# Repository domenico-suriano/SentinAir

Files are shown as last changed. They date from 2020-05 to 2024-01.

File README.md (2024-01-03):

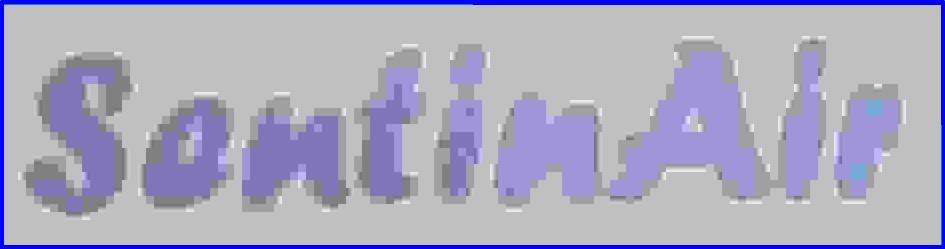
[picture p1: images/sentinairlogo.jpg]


Project designer and developer

Dr. Domenico Suriano , domenico.suriano@enea.it

# Description

SentinAir is a device designed for data acquisition from diverse types of instruments, sensors or devices. This system was at first developed for air pollutant monitoring activities, but it can also be used in other fields. Through this tool, you can acquire data from gas sensors or devices that you can plug into SentinAir system by USB, Ethernet, serial, or I2C ports. This system is useful especially in activities performed far from the laboratory facilities. The minimum requirement necessary to use the SentinAir device is a 220 Volt a.c. power source. The system can be controlled from the remote through internet wireless connections or through the Wi-Fi LAN set up by the SentinAir device as soon as it starts up. You can use SentinAir, for example, as a portable monitoring unit for air pollutant concentration detection; or, for evaluating device, instrument and sensor performances. By clicking on the pictures below you can see an explanatory video about the SentinAir use. You can find detailed information about how to set up and use SentinAir in the [user guide](https://github.com/domenico-suriano/SentinAir/blob/master/guide/sentinair-user-guide-2.0.pdf) released in the "guide" folder of this repository. The description of the SentinAir system and its use are also shown in four scientific articles: [A portable air quality monitoring unit and a modular, flexible tool for on-field evaluation and calibration of low-cost gas sensors](https://doi.org/10.1016/j.ohx.2021.e00198) published on HardwareX by Elsevier, [SentinAir system software: A flexible tool for data acquisition from heterogeneous sensors and devices](https://doi.org/10.1016/j.softx.2020.100589) published on "SoftwareX" by Elsevier, [Design and Development of a Flexible, Plug-and-Play, Cost-Effective Tool for on-Field Evaluation of Gas Sensors](https://doi.org/10.1155/2020/8812025) published on "Journal of Sensors" by Hindawi, and [Assessment of the Performance of a Low-Cost Air Quality Monitor in an Indoor Environment through Different Calibration Models](https://doi.org/10.3390/atmos13040567) published on "Atmosphere" by MDPI. I hope it will be useful to you.

# SentinAir software quick installation
This is a quick procedure to install the SentinAir software making the minimum steps. If you desire a higher level of customization, you can refer to the “SentinAir software installation” chapter of the [user guide](https://github.com/domenico-suriano/SentinAir/blob/master/guide/sentinair-user-guide-2.0.pdf) released in this repository. To install SentinAir, download the [last SentinAir SD card image file](https://drive.google.com/file/d/1KaBjFTMJjB79ryGpAMCCBvThq09m7BA6/view?usp=sharing) (file size of 720 Mb), unzip the file, then write it in a SD card having at least 2 GB of memory space (4GB recommended) by using, for example, Win32diskimage.exe program (for Windows operative systems). Finally, insert the SD card in the slot of the Raspberry PI board.

# Using SentinAir
After following the "quick installation" procedure, plug into one of the system ports your sensors/devices/instruments and give power to the device. Wait for a few of seconds, you will see the green light asynchronously blinking (this indicates that the system is starting up). After few seconds, the yellow light will start blinking fastly. This means that the system is performing the port scanning and the devices/sensor/instrument connection. Wait for few tens of seconds, then the red check light will turn on. When the yellow light stops blinking and turns on, the system is ready and it is already performing the data acquisition. To shut down SentinAir, press for few seconds the "stop button", then the yellow check light will start blinking. Wait for each light turns off, then unplug the power cable. For more detials to use the SentinAir system, please, refer to the [user guide](https://github.com/domenico-suriano/SentinAir/blob/master/guide/sentinair-user-guide-2.0.pdf) released in this repository. An overview of the SentinAir system use is shown in the video you can see by clicking on the pictures at the bottom of this page.
Here below are summarized the instruments which drivers have been already developed and incorporated in the sentinAIr software, and therefore, readily usable with sentinAir.
| Device | Device driver | Connection interface | Supplier or manufacturer |
|     :---:    |            :---:            |                      :---:                   |                         :---:                        |
|106L GO3 pro package (CO2and O3 monitor)|[go3.py](https://github.com/domenico-suriano/SentinAir/blob/master/sentinair/devices/go3.py)|USB|[2B technologies](https://www.twobtech.com)|
|405nm (NOx monitor)|[nox405.py ](https://github.com/domenico-suriano/SentinAir/blob/master/sentinair/devices/nox405.py)|USB|2B technologies|
|CO12M (CO chemical analyzer)|[co12m.py](https://github.com/domenico-suriano/SentinAir/blob/master/sentinair/devices/co12m.py) |Ethernet port|[Environnement](https://www.envea.global)|
|AF22M (SO2 chemical analyzer)|[af22.py ](https://github.com/domenico-suriano/SentinAir/blob/master/sentinair/devices/af22.py)|Ethernet port|Environnement|
|AC32M (NOx chemical analyzer)|[ac32.py](https://github.com/domenico-suriano/SentinAir/blob/master/sentinair/devices/ac32.py) |Ethernet port|Environnement|
|O342M (O3 chemical analyzer)|[o342.py](https://github.com/domenico-suriano/SentinAir/blob/master/sentinair/devices/o342.py) |Ethernet port|Environnement|
|VOC72M (VOCchemical analyzer)|[v72m.py](https://github.com/domenico-suriano/SentinAir/blob/master/sentinair/devices/v72m.py) |Ethernet port|Environnement|

Here below are listed the sensors having a I2C, TTL serial port, or USB hardware interface, which drivers have been already developed and incorporated in the sentinAIr software, and therefore, readily usable with sentinAir. This list does not include the sensors featured by only an analog output interface.

| Sensor | Sensor driver | Connection interface | Supplier or manufacturer |
|     :---:    |            :---:            |                      :---:                   |                         :---:                        |
|BME280 (atmospheric pressure, temperature, and relative humidity)|[bme280.py](https://github.com/domenico-suriano/SentinAir/blob/master/sentinair/devices/bme280.py)|I2C|[Bosch Sensortec](https://www.bosch-sensortec.com)|
|BH1750 (luxmeter)|[bh1750.py](https://github.com/domenico-suriano/SentinAir/blob/master/sentinair/devices/bh1750.py) |I2C|[ROHM semiconductor](https://www.rohm.com)|
|PMS5003 (PM sensor)|[pms5003.py](https://github.com/domenico-suriano/SentinAir/blob/master/sentinair/devices/pms5003.py) |TTL serial port|[Plantower](https://www.plantower.com/en/)|
|PMS3003 (PM sensor)|[pms3003.py ](https://github.com/domenico-suriano/SentinAir/blob/master/sentinair/devices/pms3003.py)|TTL serial port|Plantower|
|MHZ19 (CO2 sensor)|[mhz19.py](https://github.com/domenico-suriano/SentinAir/blob/master/sentinair/devices/mhz19.py) |TTL serial port|[Winsen](https://www.winsen-sensor.com)|
|IRC-A1 (CO2 sensor)|[irca1.py](https://github.com/domenico-suriano/SentinAir/blob/master/sentinair/devices/irca1.py) |USB|[Alphasense](https://www.alphasense.com/product_type/target-gas/)|
|SPS30 (PM sensor)|[sps30.py](https://github.com/domenico-suriano/SentinAir/blob/master/sentinair/devices/sps30.py) |TTL serial port|[Sensirion](https://sensirion.com)|

In order to use the sensors featured by just the analog hardware interface, drivers for some Analog-to-DIgital Converter (ADC) boards have been already developed and incorporated in the SentinAIr software. Currently, they are the [ADC Pi board](https://www.abelectronics.co.uk/p/69/adc-pi-raspberry-pi-analogue-to-digital-converter) (which driver is [mcp342x.py](https://github.com/domenico-suriano/SentinAir/blob/master/sentinair/devices/mcp342x.py)) by [ABelectronics](https://www.abelectronics.co.uk/), the [Multisensor board](https://www.tecnosens.it/en/multisensor) (which driver is [multisensor_board.py](https://github.com/domenico-suriano/SentinAir/blob/master/sentinair/devices/multisensor_board.py)) by [Tecnosens](https://www.tecnosens.it/en), and the Lcss adapter which is an open source project you can find [here](https://github.com/domenico-suriano/Lcss-adapter-board).

In the list shown below, there are some examples of sensors featured by an analog output signal that can be readily used in the SentinAir system. The list does not cover every sensor or device available on the market usable with SentinAir, because its purpose is just to provide an idea about the flexibility of the system proposed. Therefore, this is a partial list which wants to provide some examples. Moreover, we must consider that any analog sensor has to be used through its support board, usually provided by the manufacturer, or the supplier, or built by the user, and one of the boards acting as adapter to the SentinAir system, such as: the ADC Pi board, the LCSS adapter, or the Multisensor board.

| Sensor | Support board name | Adapter board| Sensor supplier or manufacturer |
|     :---:    |            :---:            |                      :---:                   |                         :---:                        |
|CO-BX (CO sensor)|[ISB by Alphasense](https://www.alphasense.com/products/support-circuits-air/) or [Alphasense-B4-multisensor-board](https://github.com/domenico-suriano/Alphasense-B4-multisensor-board) |ADC Pi or LCSS adapter|[Alphasense](https://www.alphasense.com)|
|NO2-B43F (NO2 sensor)|ISB by Alphasense or Alphasense-B4-multisensor-board|ADC Pi or LCSS adapter|Alphasense|
|NO-B4 (NO sensor)|ISB by Alphasense |ADC Pi or LCSS adapter|Alphasense|
|OX-B431 (O3 sensor)|ISB by Alphasense or Alphasense-B4-multisensor-board|ADC Pi or LCSS adapter|Alphasense|
|SO2-B4 (SO2 sensor)|ISB by Alphasense or Alphasense-B4-multisensor-board|ADC Pi or LCSS adapter|Alphasense|
|H2S-B4 (H2S sensor)|ISB by Alphasense or Alphasense-B4-multisensor-board|ADC Pi or LCSS adapter|Alphasense|
|CO-A4 (CO sensor)|[AFE by Alphasense](https://www.alphasense.com/products/support-circuits-air/)|ADC Pi or LCSS adapter|Alphasense|
|NO-A4 (NO sensor)|AFE by Alphasense|ADC Pi or LCSS adapter|Alphasense|
|SO2-A4 (SO2 sensor)|AFE by Alphasense|ADC Pi or LCSS adapter|Alphasense|
|OX-A431 (O3 sensor)|AFE by Alphasense|ADC Pi or LCSS adapter|Alphasense|
|H2S-A4 (H2S sensor)|AFE by Alphasense|ADC Pi or LCSS adapter|Alphasense|
|PID-A12 (VOC sensor)|AFE by Alphasense|ADC Pi or LCSS adapter|Alphasense|
|PID-AH2 (VOC sensor)|AFE by Alphasense|ADC Pi or LCSS adapter|Alphasense|
|GS+4CO (CO sensor)|[AFE by TEcnosens](https://www.tecnosens.it/en/application-sectors/multigas-monitor/multisensor-board)|[Multisensor board by Tecnosens](https://www.tecnosens.it/en/application-sectors/multigas-monitor/multisensor-board)|[DDScientific](https://www.ddscientific.com)|
|GS+4ETO (ETO sensor)|AFE by TEcnosens|Multisensor board by Tecnosens|DDScientific|
|GS+4NH3-100 (NH3 sensor)|AFE by TEcnosens|Multisensor board by Tecnosens|DDScientific|
|GS+4NO (NO sensor)|AFE by TEcnosens|Multisensor board by Tecnosens|DDScientific|
|GS+4NO2 (NO2 sensor)|AFE by TEcnosens|Multisensor board by Tecnosens|DDScientific|
|GS+4CL2 (Cl2 sensor)|AFE by TEcnosens|Multisensor board by Tecnosens|DDScientific|
|GS+4SO2 (SO2 sensor)|AFE by TEcnosens|Multisensor board by Tecnosens|DDScientific|
|TDS 0035(CH4 sensor)|AFE by TEcnosens|Multisensor board by Tecnosens|[Dynament](https://www.dynament.com/data-old/premier-series/)|
|TDS 0058(CO2 sensor)|AFE by TEcnosens|Multisensor board by Tecnosens|[Dynament](https://www.dynament.com/data-old/premier-series/)|
|SP61 (O3 sensor)|[A1320301-SP61-01 by Nissha](https://www.fisinc.co.jp/en/products/products_search.html?Cat=Cat2)|ADC Pi or LCSS adapter|[Nissha-Fis](https://www.fisinc.co.jp/en/)|
|SP61 (O3 sensor)|A1320301-SP61-02 by Nissha|ADC Pi|Nissha-Fis|
|SPS-AQ2-01 (VOC sensor)|EVM-SP-02-SP3S by Nissha|ADC Pi|Nissha-Fis|
|SB-xx (SB series sensor for various gases)|[EVM-SB-01-xx by Nissha](https://www.fisinc.co.jp/en/products/products_search.html?Cat=Cat2)|ADC Pi|Nissha-Fis|
|SP-xx (SP series sensor for various gases)|[EVM-SP-01-xx by Nissha](https://www.fisinc.co.jp/en/products/products_search.html?Cat=Cat2)|ADC Pi|Nissha-Fis|
|TGS26xx (TGS26 series sensor for various gases)|[EM26 by Figaro](https://www.figarosensor.com/product/evaluation-board/)|ADC Pi|[Figaro](https://www.figarosensor.com)|
|FECSxx (FECS series sensor for various gases)|[EM-FECS(B) by Figaro](https://www.figarosensor.com/product/evaluation-board/)|ADC Pi|Figaro|
|ME2-CO (CO sensor)|[ZE07-CO by Winsen](https://www.winsen-sensor.com/sensors/co-sensor/ze07-co.html)|ADC Pi or LCSS adapter|[Winsen](https://www.winsen-sensor.com/)|

# Last Updates

16 december 2023

-a) removed the lighttpd http server

-b) updated "sentinair-system-manager.py" to optimize the hourly and daily calulations, to incorporate the http server and to add the graphical user interface through the new web pages

-c) modified the structure of the sentinair software directories

-d) updated "sentinair-system-installer.py" to improve the "user-friendly" grade

26 september 2022

-a) updated "sentinair-system-manager.py" to fix a bug in logging the device scanning reports

-b) added the drivers for SPS30 (PM sensor), PMS5003 (PM sensor), and MHZ19 (CO2 sensor)

2 february 2021

-a) updated "sentinair-system-manager.py" to modify the check light behaviour

-b) added the driver for bme280 (temperature, humidity, and atmospheric pressure sensor)

11 november 2020:

-a) updated "sentinair-system-manager.py" to support I2C devices

-b) added drivers for bh1750 (luxmeter) and mcp342x (ADC Pi converter)

-c) updated the user guide. More clarifications and examples concerning "How to write new device drivers". Added information about the use of the ADC Pi.

-d) added device driver templates to facilitate the process of writing new device drivers (see the user guide).

-e) published the release of the version 1.2

-f) [SentinAir SD card image file](https://drive.google.com/file/d/1Ex4GyDE1UydjNPgzCsWaSeaUH6ddkkUb/view?usp=sharing) updated.

7 october 2020:

-a) minor bugs fixed.

-b) the red check light now blinks during the port scanning at start-up time.

-c) configuration of the module "imap-smtp-interface.py" by editing the file "mail-config.sentinair" (please refer to the [user guide](https://github.com/domenico-suriano/SentinAir/blob/master/guide/sentinair-system-user-guide.pdf) for details),

-d) User guide updated,

-e) release [sentinair_1.0.zip](https://github.com/domenico-suriano/SentinAir/releases/download/1.0/sentinair-1.0.zip) updated,

-f) [SentinAir SD card image file](https://drive.google.com/file/d/1AfPUjvr3tC3ymnK-TsBThjoi5kFb1ZuD/view?usp=sharing) updated.

30 september 2020:

-a) user guide updated,

-b) some minor bugs fixed.

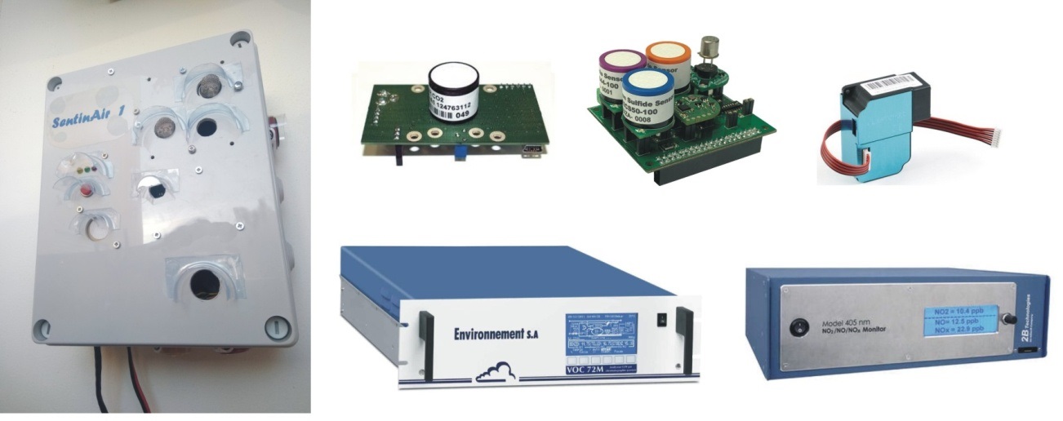
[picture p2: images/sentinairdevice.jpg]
sentinair (https://youtu.be/oAHfk2gzcIE)

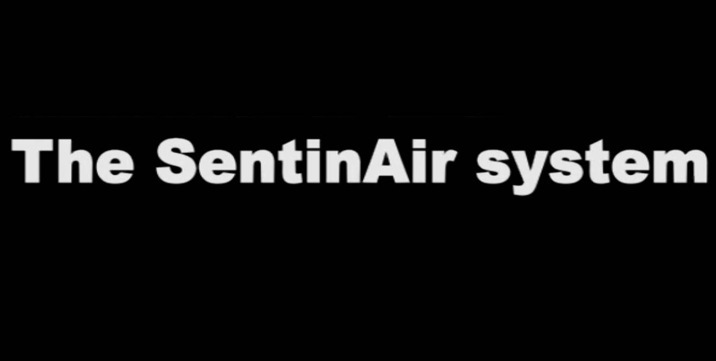
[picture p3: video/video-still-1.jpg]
how to use SentinAir (https://youtu.be/oAHfk2gzcIE)


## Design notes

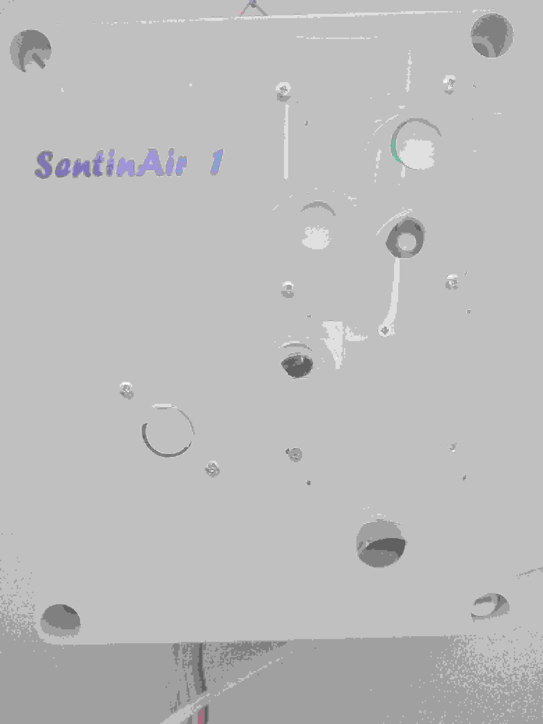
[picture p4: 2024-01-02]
sentinair/img/sentinair.png

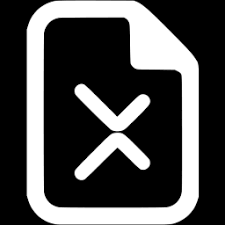
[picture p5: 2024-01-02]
sentinair/img/file_not_found.png

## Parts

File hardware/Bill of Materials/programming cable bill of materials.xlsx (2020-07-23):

Programming cable
Item | Quantity | Reference | CASE | UNIT PRICE ($) | SUPPLIER | SUPPLIER PART NO. | MANUFACTURER PART NO.
1 | 1 | RJ11 | RJ11 | 0.27 | digikey.com | 609-5354-ND | 54601-906001WPLF
1 | 1 | 5 position male | 2 mm pitch SIL | 0.85 | digikey.com | SAM15859-ND | TMM-105-03-G-S
 |  |  |  | 1.12

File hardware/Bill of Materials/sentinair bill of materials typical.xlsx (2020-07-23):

Bill of Materials of SentinAir in typical hardware configuration
Item | Quantity | Reference | UNIT PRICE ($) | SUPPLIER | SUPPLIER PART NO. | MANUFACTURER PART NO.
1 | 1 | LED green | 0.2 | digikey.com | C5SMF-GJF-CV0Y0792CT-ND | C5SMF-GJF-CV0Y0792
1 | 1 | LED red | 0.14 | digikey.com | C5SMF-RJF-CT0W0BB1-ND | C5SMF-RJF-CT0W0BB1
1 | 1 | LED yellow | 0.41 | digikey.com | 1516-QBL8Y30C-ND | QBL8Y30C
1 | 1 | PUSH button | 1.73 | digikey.com | 2368-54-556-2-ND | 54-556-2
1 | 3 | R1 | 0.1 | digikey.com | CF18JT120RCT-ND | CF18JT120R
 |  | R2 | 0.1 | digikey.com | CF18JT120RCT-ND | CF18JT120R
 |  | R3 | 0.1 | digikey.com | CF18JT120RCT-ND | CF18JT120R
1 | 1 | Prototype board | 4.95 | digikey.com | 1528-2171-ND | 2670
1 | 1 | Huawei e303 hspa modem | 15.9 | alibaba.com |  | E303 huawei 3g modem
1 | 1 | switching power supply | 12.73 | it.rs-online.com | 413-673 | RS-15-5
1 | 1 | enclosure | 14.9 | amazon.it | B0151KNMB2 | B-240
1 | 1 | PC sheet | 19.03 | it.rs-online.com | 769-8736 | 769-8736
1 | 1 | LCSS adapter board | 92.97 | see lcss board bill of materials.xlsx file
1 | 1 | programming cable | 1.12 | digikey.com | see lcss programming cable bill of materials.xlsx file
1 | 1 | SD card 8 Gb class 10 | 8.1 | amazon.it |  | Transcend TS8GUSDCU1
 |  |  | 172.48

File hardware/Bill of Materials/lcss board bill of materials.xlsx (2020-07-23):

LCSS adapter board Bill Of Materials
Item | Quantity | Reference | Part | CASE | UNIT PRICE ($) | BATCH PRICE ($) | SUPPLIER | SUPPLIER PART NO. | MANUFACTURER PART NO.
1 | 3 | C1 | 100n | 805 | 0.1 |  | digikey.com | 399-1177-1-ND | KEMET C0805C104Z5VACTU
 |  | C10 | 100n | 805 | 0.1 |  | digikey.com | 399-1177-1-ND | KEMET C0805C104Z5VACTU
 |  | C12 | 100n | 805 | 0.1 |  | digikey.com | 399-1177-1-ND | KEMET C0805C104Z5VACTU
2 | 7 | C2 | 10u | 805 | 0.16 |  | digikey.com | 399-4925-1-ND | KEMET C0805C106K8PACTU
 |  | C5 | 10u | 805 | 0.16 |  | digikey.com | 399-4925-1-ND | KEMET C0805C106K8PACTU
 |  | C6 | 10u | 805 | 0.16 |  | digikey.com | 399-4925-1-ND | KEMET C0805C106K8PACTU
 |  | C7 | 10u | 805 | 0.16 |  | digikey.com | 399-4925-1-ND | KEMET C0805C106K8PACTU
 |  | C8 | 10u | 805 | 0.16 |  | digikey.com | 399-4925-1-ND | KEMET C0805C106K8PACTU
 |  | C15 | 10u | 805 | 0.16 |  | digikey.com | 399-4925-1-ND | KEMET C0805C106K8PACTU
 |  | C20 | 10u | 805 | 0.16 |  | digikey.com | 399-4925-1-ND | KEMET C0805C106K8PACTU
3 | 2 | C3 | 22p | 805 | 0.1 |  | digikey.com | 399-1113-1-ND | KEMET C0805C220J5GACTU
 |  | C4 | 22p | 805 | 0.1 |  | digikey.com | 399-1113-1-ND | KEMET C0805C220J5GACTU
4 | 9 | C9 | 10n | 805 | 0.1 |  | digikey.com | 399-1159-1-ND | KEMET C0805C103K1RACTU
 |  | C13 | 10n | 805 | 0.1 |  | digikey.com | 399-1159-1-ND | KEMET C0805C103K1RACTU
 |  | C14 | 10n | 805 | 0.1 |  | digikey.com | 399-1159-1-ND | KEMET C0805C103K1RACTU
 |  | C16 | 10n | 805 | 0.1 |  | digikey.com | 399-1159-1-ND | KEMET C0805C103K1RACTU
 |  | C17 | 10n | 805 | 0.1 |  | digikey.com | 399-1159-1-ND | KEMET C0805C103K1RACTU
 |  | C18 | 10n | 805 | 0.1 |  | digikey.com | 399-1159-1-ND | KEMET C0805C103K1RACTU
 |  | C19 | 10n | 805 | 0.1 |  | digikey.com | 399-1159-1-ND | KEMET C0805C103K1RACTU
 |  | C21 | 10n | 805 | 0.1 |  | digikey.com | 399-1159-1-ND | KEMET C0805C103K1RACTU
 |  | C22 | 10n | 805 | 0.1 |  | digikey.com | 399-1159-1-ND | KEMET C0805C103K1RACTU
5 | 1 | C11 | 4.7u | 805 | 0.21 |  | digikey.com | 399-3134-1-ND | KEMET C0805C475K9PACTU
6 | 1 | D1 | BAV20WS | SOD323 | 0.2 |  | digikey.com | BAV20WSTPMSCT-ND | BAV20WS-TP
7 | 1 | D2 | PMEG3010EH | DO-214AC (SMA) | 0.34 |  | digikey.com | 1727-3869-1-ND | PMEG3010EH
14 | 1 | J7 | icsp | 2.0 mm pitch | 1.16 |  | digikey.com | 952-1352-5-ND | Harwin M22-7130542
29 | 1 | J22 | sens plug | 2.54 mm pitch | 1.1 |  | digikey.com | 952-2260-ND | Harwin M20-9773646
30 | 1 | L1 | 30 ohm | 1206 | 0.75 |  | digikey.com | 490-16913-1-ND | Murata LQW31HN33NJ03L
31 | 1 | Q1 | IRLML9301TRPbF | SOT23 | 0.37 |  | digikey.com | IRLML9301TRPBFCT-ND | IRLML9301TRPBF
32 | 1 | Q2 | DMP2160UW | SOT23 | 0.28 | 14.22 | it.rs-online.com | 751-4240 | DMP2160UW-7
33 | 1 | Q3 | ZXT11N20DF | SOT23 | 0.61 |  | digikey.com | ZXT11N20DFCT-ND | ZXT11N20DFTA
34 | 1 | R1 | 10k | 805 | 0.1 |  | digikey.com | 311-10.0KCRCT-ND | RC0805FR-0710KL
35 | 3 | R2 | 330 | 805 | 0.1 |  | digikey.com | A129743CT-ND | CRGCQ0805F330R
 |  | R3 | 330 | 805 | 0.1 |  | digikey.com | A129743CT-ND | CRGCQ0805F330R
 |  | R6 | 330 | 805 | 0.1 |  | digikey.com | A129743CT-ND | CRGCQ0805F330R
36 | 6 | R4 | 56k | 805 | 0.1 |  | digikey.com | A126377CT-ND | CRG0805F56K
 |  | R5 | 56k | 805 | 0.1 |  | digikey.com | A126377CT-ND | CRG0805F56K
 |  | R7 | 56k | 805 | 0.1 |  | digikey.com | A126377CT-ND | CRG0805F56K
 |  | R8 | 56k | 805 | 0.1 |  | digikey.com | A126377CT-ND | CRG0805F56K
 |  | R11 | 56k | 805 | 0.1 |  | digikey.com | A126377CT-ND | CRG0805F56K
 |  | R13 | 56k | 805 | 0.1 |  | digikey.com | A126377CT-ND | CRG0805F56K
37 | 2 | R9 | 22k | 805 | 0.1 |  | digikey.com | A129765CT-ND | CRGCQ0805F22K
 |  | R10 | 22k | 805 | 0.1 |  | digikey.com | A129765CT-ND | CRGCQ0805F22K
38 | 1 | R12 | 3k | 805 | 0.1 |  | digikey.com | A126368CT-ND | CRG0805F3K0
39 | 8 | R14 | 500k | SMD/2.2x0.81x2.81 | 0.89 |  | digikey.com | P2N504CT-ND | EVM-2NSX80B55
 |  | R15 | 500k | SMD/2.2x0.81x2.82 | 0.89 |  | digikey.com | P2N504CT-ND | EVM-2NSX80B56
 |  | R22 | 500k | SMD/2.2x0.81x2.83 | 0.89 |  | digikey.com | P2N504CT-ND | EVM-2NSX80B57
 |  | R23 | 500k | SMD/2.2x0.81x2.84 | 0.89 |  | digikey.com | P2N504CT-ND | EVM-2NSX80B58
 |  | R30 | 500k | SMD/2.2x0.81x2.85 | 0.89 |  | digikey.com | P2N504CT-ND | EVM-2NSX80B59
 |  | R31 | 500k | SMD/2.2x0.81x2.86 | 0.89 |  | digikey.com | P2N504CT-ND | EVM-2NSX80B60
 |  | R38 | 500k | SMD/2.2x0.81x2.87 | 0.89 |  | digikey.com | P2N504CT-ND | EVM-2NSX80B61
 |  | R39 | 500k | SMD/2.2x0.81x2.88 | 0.89 |  | digikey.com | P2N504CT-ND | EVM-2NSX80B62
40 | 8 | R16 | 0 | 805 | 0.1 |  | digikey.com | 311-0.0CRCT-ND | RC0805FR-070RL
 |  | R17 | 0 | 805 | 0.1 |  | digikey.com | 311-0.0CRCT-ND | RC0805FR-070RL
 |  | R24 | 0 | 805 | 0.1 |  | digikey.com | 311-0.0CRCT-ND | RC0805FR-070RL
 |  | R25 | 0 | 805 | 0.1 |  | digikey.com | 311-0.0CRCT-ND | RC0805FR-070RL
 |  | R32 | 0 | 805 | 0.1 |  | digikey.com | 311-0.0CRCT-ND | RC0805FR-070RL
 |  | R33 | 0 | 805 | 0.1 |  | digikey.com | 311-0.0CRCT-ND | RC0805FR-070RL
 |  | R40 | 0 | 805 | 0.1 |  | digikey.com | 311-0.0CRCT-ND | RC0805FR-070RL
 |  | R41 | 0 | 805 | 0.1 |  | digikey.com | 311-0.0CRCT-ND | RC0805FR-070RL
41 | 16 | R18 | 100k | 805 | 0.1 |  | digikey.com | 311-100KCRCT-ND | RC0805FR-07100KL
 |  | R19 | 100k | 805 | 0.1 |  | digikey.com | 311-100KCRCT-ND | RC0805FR-07100KL
 |  | R20 | 100k | 805 | 0.1 |  | digikey.com | 311-100KCRCT-ND | RC0805FR-07100KL
 |  | R21 | 100k | 805 | 0.1 |  | digikey.com | 311-100KCRCT-ND | RC0805FR-07100KL
 |  | R26 | 100k | 805 | 0.1 |  | digikey.com | 311-100KCRCT-ND | RC0805FR-07100KL
 |  | R27 | 100k | 805 | 0.1 |  | digikey.com | 311-100KCRCT-ND | RC0805FR-07100KL
 |  | R28 | 100k | 805 | 0.1 |  | digikey.com | 311-100KCRCT-ND | RC0805FR-07100KL
 |  | R29 | 100k | 805 | 0.1 |  | digikey.com | 311-100KCRCT-ND | RC0805FR-07100KL
 |  | R34 | 100k | 805 | 0.1 |  | digikey.com | 311-100KCRCT-ND | RC0805FR-07100KL
 |  | R35 | 100k | 805 | 0.1 |  | digikey.com | 311-100KCRCT-ND | RC0805FR-07100KL
 |  | R36 | 100k | 805 | 0.1 |  | digikey.com | 311-100KCRCT-ND | RC0805FR-07100KL
 |  | R37 | 100k | 805 | 0.1 |  | digikey.com | 311-100KCRCT-ND | RC0805FR-07100KL
 |  | R42 | 100k | 805 | 0.1 |  | digikey.com | 311-100KCRCT-ND | RC0805FR-07100KL
 |  | R43 | 100k | 805 | 0.1 |  | digikey.com | 311-100KCRCT-ND | RC0805FR-07100KL
 |  | R44 | 100k | 805 | 0.1 |  | digikey.com | 311-100KCRCT-ND | RC0805FR-07100KL
 |  | R45 | 100k | 805 | 0.1 |  | digikey.com | 311-100KCRCT-ND | RC0805FR-07100KL
42 | 1 | S1 | USB-connB | PHT(usbB) | 1.23 |  | it.rs-online.com | 748-0866 | 61400416121
43 | 1 | U1 | RN42XV (optional) |  | 19.95 |  | digikey.com | RN42XVU-I/RM-ND | RN42XVU-I/RM
44 | 1 | U2 | TC1047A | SOT-23B | 0.62 |  | digikey.com | TC1047AVNBCT-ND | TC1047AVNBTR
45 | 1 | U3 | HIH5031 | SMD/4.17x8.59x2.67mm | 27.27 |  | digikey.com | 480-4967-ND | HIH-5031-001S
46 | 1 | U4 | PIC18F4685 | TQFP44 | 8.97 |  | digikey.com | PIC18F4685T-I/PTCT-ND | PIC18F4685T-I/PT
47 | 1 | U5 | LD29080DT33-DPAK | D-PAK | 1.19 |  | digikey.com | 497-4243-1-ND | LD29080DT33R
48 | 1 | U6 | MCP73832-SOT23 | SOT23 | 0.56 |  | digikey.com | MCP73832T-3ACI/OTCT-ND | MCP73832T-3ACI/OT
49 | 1 | U7 | FT232RL | SSOP-28 | 4.5 |  | digikey.com | 768-1007-1-ND | FT232RL-REEL
50 | 2 | U8 | AD8609 | SOICN-ARZ14 | 5.06 |  | digikey.com | AD8609ARZ-ND | AD8609ARZ
 |  | U9 | AD8609 | SOICN-ARZ14 | 5.06 |  | digikey.com | AD8609ARZ-ND | AD8609ARZ
51 | 1 | X1 | 10 Mhz | HC-49/US | 0.2 |  | digikey.com | 2151-AS-10.000-20-3030-SMD-TRCT-ND | AS-10.000-20-3030-SMD-TR
 |  |  |  |  | 92.97

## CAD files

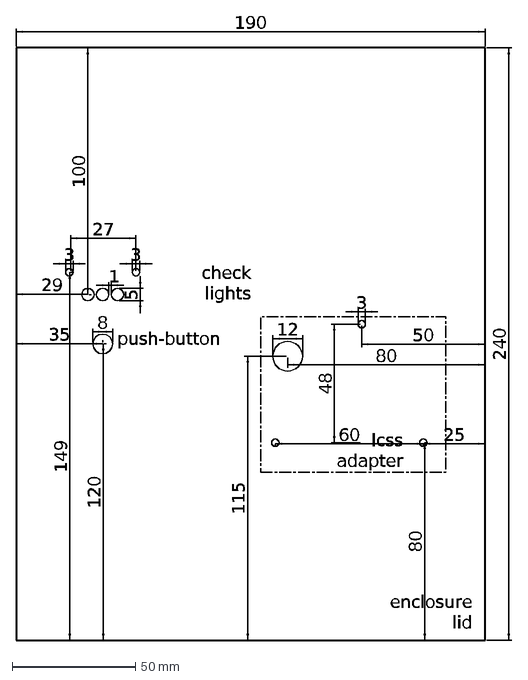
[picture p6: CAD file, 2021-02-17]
hardware/drawings/enclosure-lid.dxf
190
240
35
120
8
enclosure lid
push-button
5
1
29
100
check lights
lcss adapter
80
25
60
50
48
12
115
3
27
149

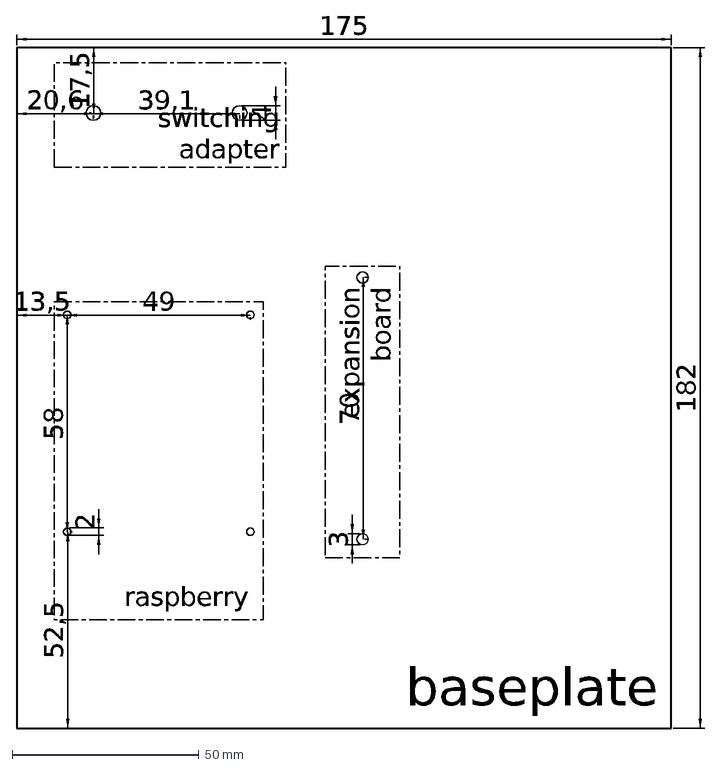
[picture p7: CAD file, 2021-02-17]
hardware/drawings/typical.dxf
baseplate
39,1
switching adapter
175
182
4
20,6
17,5
raspberry
13,5
49
58
2
52,5
70
3
expansion board

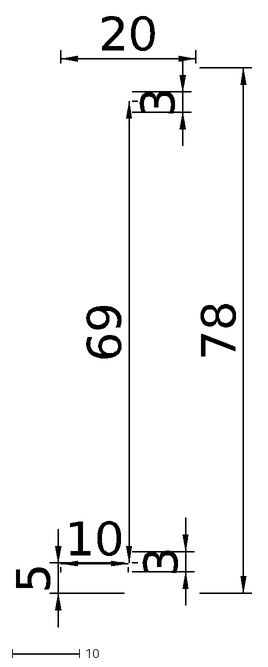
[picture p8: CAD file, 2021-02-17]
hardware/drawings/expansion.dxf
20
78
10
5
69
3

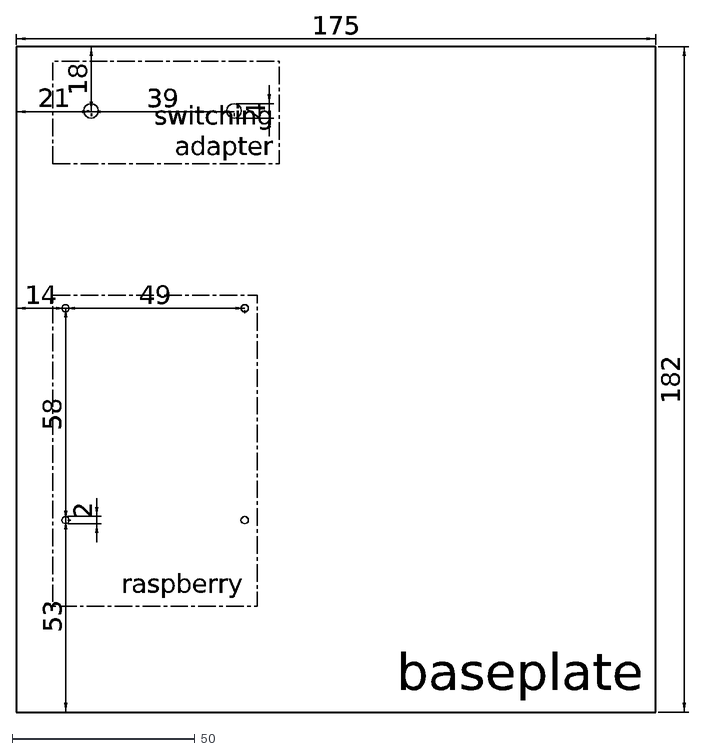
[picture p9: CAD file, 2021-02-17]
hardware/drawings/basic.dxf
baseplate
39
switching adapter
175
182
4
21
18
raspberry
14
49
58
2
53

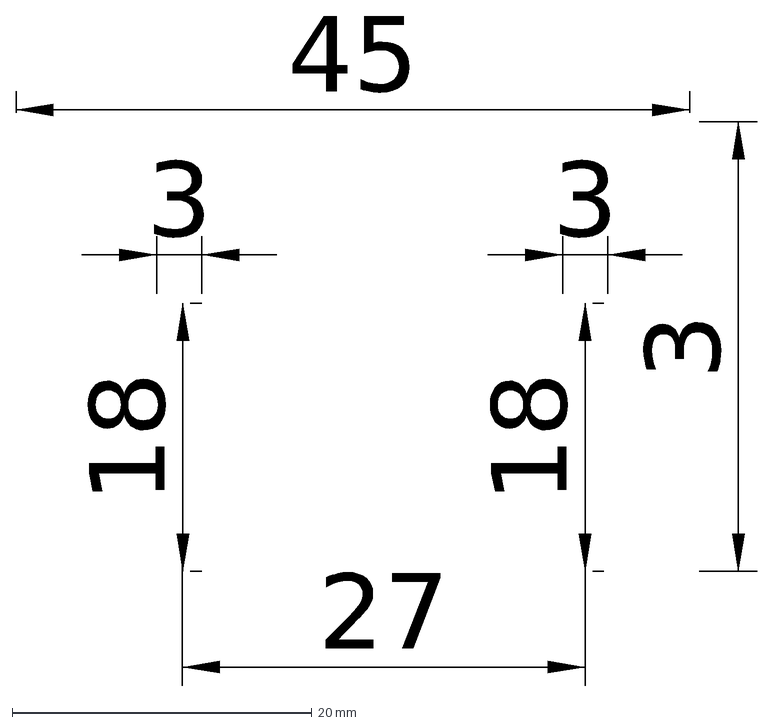
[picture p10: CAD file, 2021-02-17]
hardware/drawings/checklights.dxf
3
18
45
27

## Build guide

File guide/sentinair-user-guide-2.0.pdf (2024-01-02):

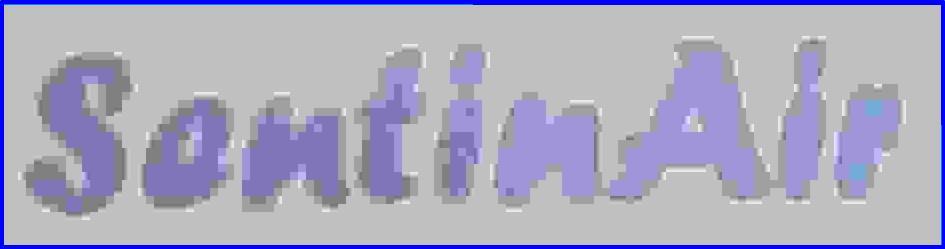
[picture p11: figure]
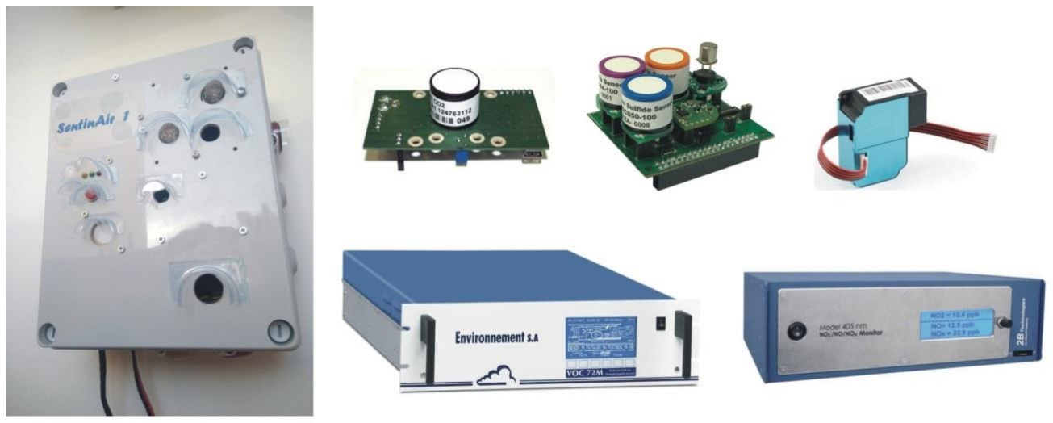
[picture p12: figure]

1

## User Guide

Project designer and developer

Dr. Domenico Suriano, (https://materiali.sostenibilita.enea.it/people/domenico-suriano) domenico.suriano@enea.it

This user guide version (v. 2.0) refers to the SentinAir system version 2.0 available at the Github SentinAir repository. (https://github.com/domenico-suriano/SentinAir)

Description

SentinAir is a device designed and developed for data acquisition from diverse types of instruments, sensors, or devices (see figure 1). The core of the system is the Raspberry 3 B+ board; therefore, the software presented in this guide can be installed either on a SentinAir device or a Raspberry 3 B+ board. Devices have to be plugged into SentinAir by USB, Ethernet, serial UART, SPI, or I2C port. Currently, the system has been tested only with devices connected by the USB, I2C, Ethernet, and serial UART port available on the Raspberry board, which is the "brain" of SentinAir. The system is based on command line interfaces, except for the web pages served by the webserver installed inside.

Figure 1: on the left, SentinAir device. On the right, some devices currently tested by SentinAir.

2

The system automatically recognizes the devices or instruments plugged into SentinAir through their specific driver, written in Python. The drivers currently developed are listed in table 1.

Table 1: device drivers developed currently for SentinAir and available in the github repository.
Sensor or device | Device driver | Connection interface | Supplier or manufacturer
BME280 (atmospheric pressure, temperature, and relative humidity) | bme280.py | I2C | Bosch Sensortec
BH1750 (luxmeter) | bh1750.py | I2C | ROHM semiconductor
MCP342x on ADC Pi board (to use devices having analog output signals) | mcp342x.py | I2C | Microchip
IRC-A1 (CO2 sensor) | irca1.py | USB | Alphasense
PMS3003 (PM sensor) | pms3003.py | TTL serial port | Plantower
PMS5003 (PM sensor) | pms5003.py | TTL serial port | Plantower
SPS30 (PM ssensor) | sps30.py | TTL serial port | Sensirion
MHZ19 (CO2 sensor) | mhz19.py | TTL serial port | Winsen
Multisensor board (to use devices having analog output signals) | multisensor_board.py | USB | Tecnosens
106L GO3 PRO package (CO2 and O3 monitor) | go3.py | USB | 2B technologies
405nm (NOx monitor) | nox405.py | USB | 2B technologies
LCSS USB adapter (to use devices having analog output signals) | lcss_adapter.py | USB | Designed and built in our lab
CO12M (CO chemical analyzer) | co12m.py | Ethernet port | Environnement
AF22M (SO2 chemical analyzer) | af22.py | Ethernet port | Environnement
AC32M (NOx chemical analyzer) | ac32.py | Ethernet port | Environnement
O342M (O3 chemical analyzer) | o342.py | Ethernet port | Environnement
VOC72M (VOC chemical analyzer) | v72m.py | Ethernet port | Environnement

## SentinAir hardware

SentinAir is a modular and flexible system. The system hardware can be assembled in a minimal (see figure 2), or a typical configuration (see figure 3). The minimal hardware is composed of:

- a Raspberry 3 B+ board
- a class 10 SD card featured by a memory capacity of at least 2 GB (4 GB recommended),.
- a 5V power source capable of providing a direct current of 3A maximum. At the moment, the system has been tested with a switching ac/dc adapter (see figure 2).

The minimal configuration allows the user to use sensors/devices/instruments featured by a USB, serial UART, I2C, or Ethernet output interface, while analog output interfaces devices must be used with one of the analog-to-digital converter boards featuring the SentinAir typical hardware configuration. Ethernet or USB devices must be connected through the Ethernet and USB sockets

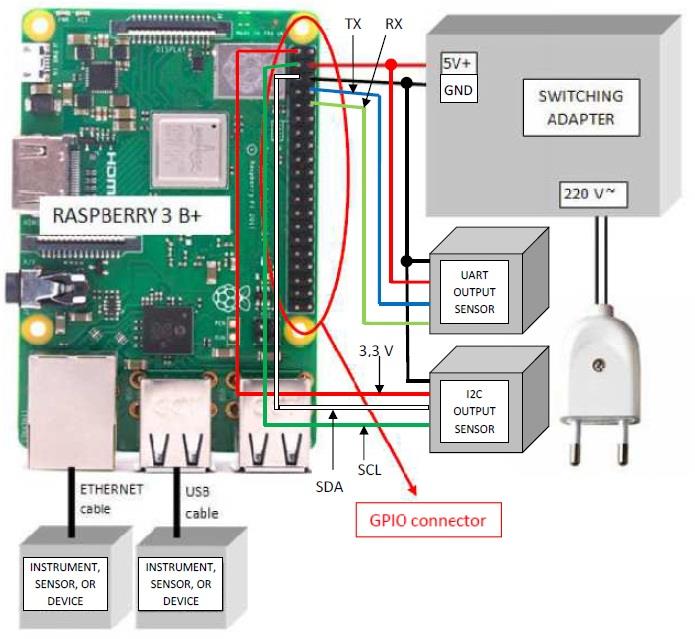
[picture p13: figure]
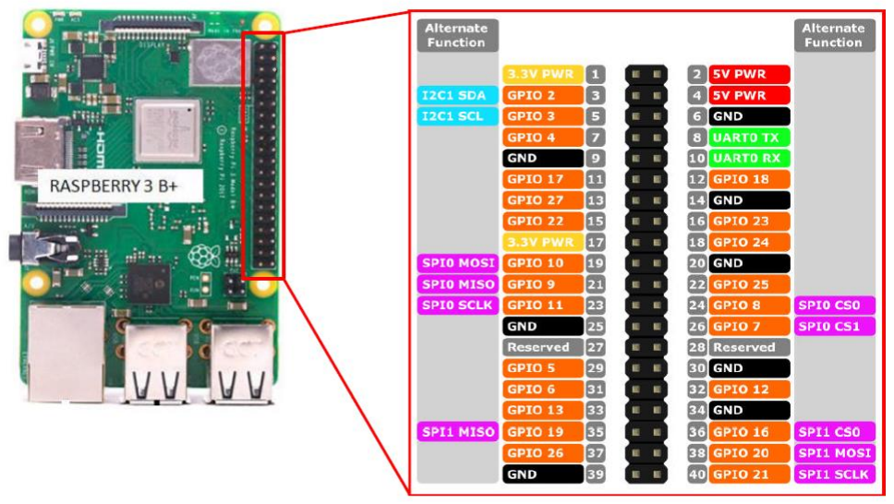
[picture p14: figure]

3

(see figure 2), while I2C and serial devices must be connected to the Raspberry GPIO connector following the indications of figure 3.

Figure 2: SentinAir hardware minimal configuration. Sensors/devices/instruments can be attached through the USB, Ethernet, Serial UART, or I2C port.

Figure 3: GPIO connector pinout. I2C devices to be used with SentinAir must connect their output to pins 3 and 5 (which is the I2C bus input). Devices having serial UART output must be connected to pins 8, 10. They can be powered through pin 2 or 4, if they need 5 Volts, otherwise, through pins 1, or 17. Device ground pins must be connected to one of the following pins: 6,9,14,20,25,30,34,39.

4

The typical hardware configuration of a SentinAir system is shown in figure 4, and it is composed of:
- A Raspberry 3 B+ board,
- a class 10 SD card featured with a memory capacity of at least 2 GB (4GB recommended),
- The check light system made of three LEDs and three 120 Ohm resistors. They are going to indicate the three possible states of the device: standby (yellow LED off), active monitoring (yellow LED on), and fault (red LED blinking),
- A push-button to properly shut down the whole system,
- A USB stick modem (the system has been tested with a Huawei E303),
- The expansion board, which is necessary to enable the simultaneous multiple connections of sensors. This board is provided by header pin connectors through which devices can be wired for the power supply or I2C bus interfacing. Three header pin connector rows provide 5, 3,3 Volts power supply, and ground connections; in addition to them, the other two pin rows offer a quick way to connect the devices SCL and the SDA signal to the mainboard I2C bus (see figure 4).
- An analog-to-digital converter board capable of giving output data on the USB, I2C, or Ethernet port. This board is necessary to convert analog outputs of sensors into digital data. In fact, the Raspberry board, on which the SentinAir system is based, has not got a built-in analog-to-digital converter; therefore, without it, the use of sensors/devices having analog output interfaces could not be possible. The user can use for this purpose any board that requires a power of 5 V and 0,2 A maximum. For example, the ADC Pi board based on the MCP3424 microprocessor by Microchip and supplied by ABelectronics (https://www.abelectronics.co.uk/) can fit the purpose. Another option is given by the LCSS adapter board (LCSS stands for Low-Cost Small commercial gas Sensors), which has been designed and developed to make the analog-to-digital conversion in an optimum way. The LCSS adapter board has been designed to minimize as much as possible the effects of the additional unwanted electronic noise, which may affect the conversion. Moreover, it has a 16-bit analog-to-digital converter that ensures a high resolution.

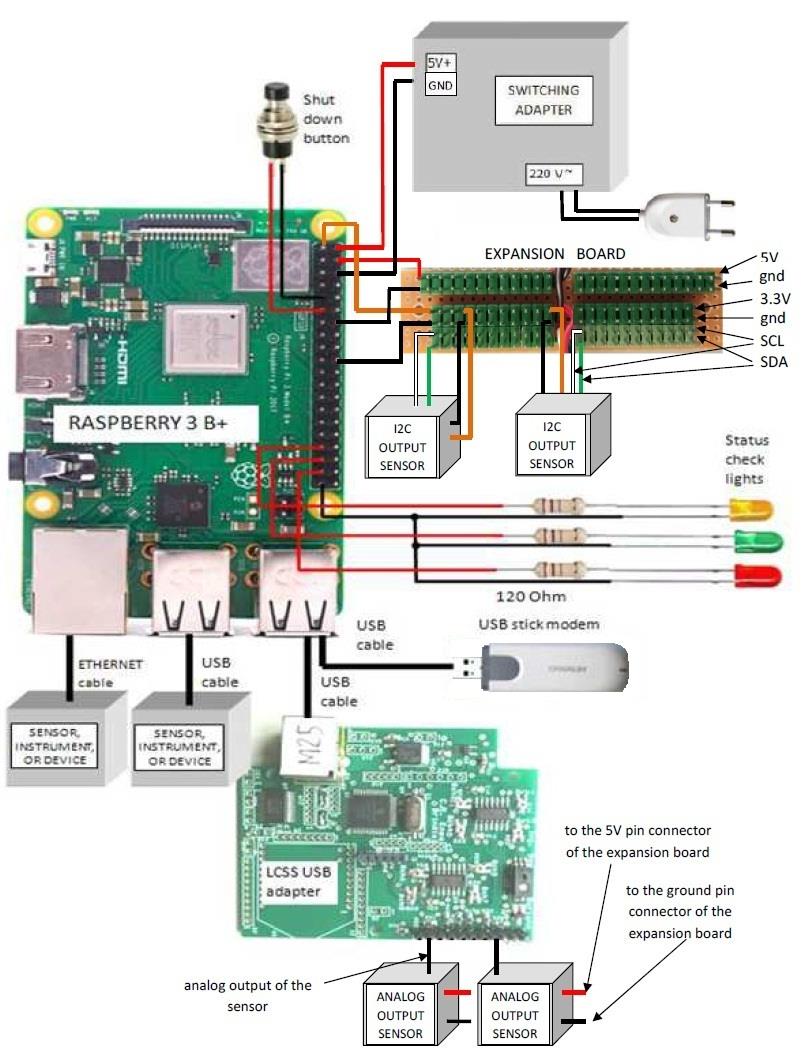
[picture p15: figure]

5

Figure 4: SentinAir hardware typical configuration. It includes an analog-to-digital converter board which enables the use of devices/sensors having analog output interfaces. This board can be the LCSS adapter or the ADC Pi by ABelectronics.

## LCSS adapter assembly and setup

The LCSS adapter board allows the use of devices having analog output interfaces, and it is powered through its USB port. It converts the input analog signals into digital data that are given as output through the USB port. The analog outputs of the devices to be used with the LCSS adapter have to be wired to the J22 connector of the LCSS board (pins 4 to 11, see figure 6). These signals must be in the range 0 - 3,3 Volts. The LCSS adapter has a built-in temperature and relative humidity sensor. Eight analog-to-digital (ADC) converters feature it. They are high resolution (16 bits) converters, each of them having a signal amplifier and electronic noise filter. The user can set

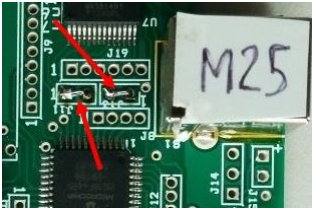
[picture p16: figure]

6

the gain of each amplifier through the resistive trimmers R14, R15, R23, R22, R30, R31, R38, R39 placed on the LCSS board (see figure 6). LCSS board can be used with the RN42XV Bluetooth adapter, even though its use is not necessary for the SentinAir system. The LCSS board is also designed to be used with rechargeable Li-Ion batteries. They have to be wired to the J15 connector (see figure 5), and they are automatically charged through the USB port. The use of batteries is not necessary for the SentinAir system.
Printed Circuit Board (PCB) files for LCSS assembly and setup can be found in the folder "lcss adapter". They were created by the "ORCAD 10.0 Layout Plus" CAD software. LCSS adapter electronic schematics are present in the same folder. The project files of the schematics were created by "ORCAD 10.0 Capture". The file named "multisensore2_0.opj" is the main project file; by opening it by "ORCAD 10.0 Capture", it is possible to view and modify all the schematics files. Schematics and PCB files are also available as "pdf" documents in the "lcss adapter/pdf files/schematics" and "lcss adapter/pdf files/pcbs" subfolders respectively. LCSS adapter board is shown fully assembled in Figures 6 and 7. When the board is fully assembled, it is necessary to wire in short-circuit the two pins of the J11 and two pins of J13, as shown in figure 5. For the first use of the LCSS board, it is advisable to set the gain of the built-in amplifiers to the unit value. This operation can be carried out by using a little screwdriver and an ohm-meter. The resistive trimmers R14, R15, R23, R22, R30, R31, R38, R39, have to be set at their minimum possible value by rotating their little top screw (see figure 6).

Figure 5: The red arrows indicate the two pins of J11and J13 to short-circuit.

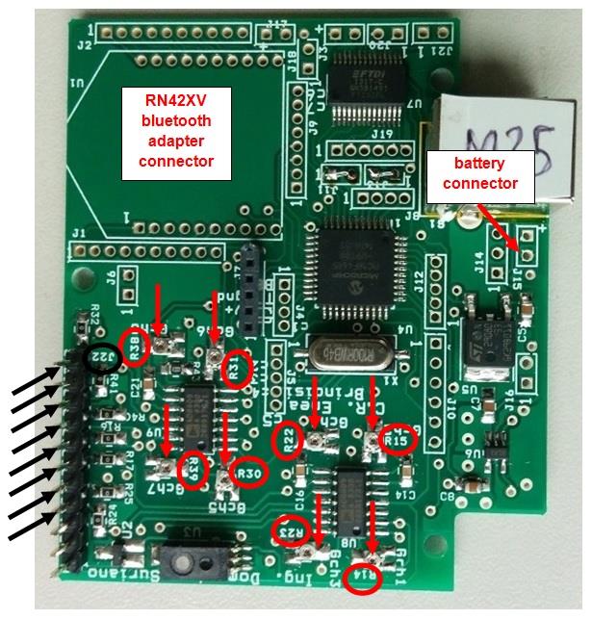
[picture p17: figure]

7

Figure 6: the black arrows and the black circle show the pins and the connector where the analog signals of the sensors have to be wired; while the red arrows and red circles indicate where the R14, R15, R23, R22, R30, R31, R38, R39 resistive trimmers are placed.

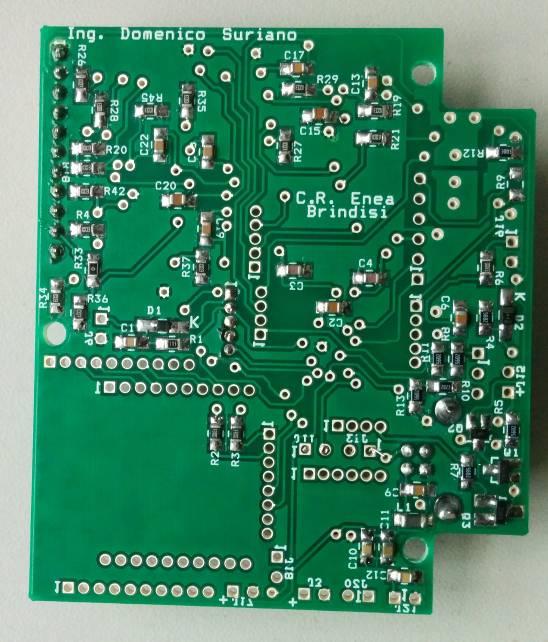
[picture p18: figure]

8

Figure 7: LCSS adapter bottom view.

The core of the LCSS adapter board is a PIC 18F4685 microcontroller by Microchip, which has to be programmed for the correct board operation. The tool needed to program the board is the "ICD2" programmer by Microchip. The necessary cable to connect the "ICD2" programmer to the LCSS board has to be assembled, as shown in figure 8. The cable is composed of an RJ11 female connector, a five positions male connector, and the wires. Optionally, the RJ11 connector can be fixed on a piece of a prototype board. The final appearance of the fully assembled cable is shown in figures 9 and 10. The electronic components needed for assembling both the LCSS adapter board and its programming cable are listed in the files placed in the subfolders "lcss adapter/bom/board" and "lcss adapter/bom/cable". In those files are also indicated the suppliers that sell all the required components. Once the programming cable and the LCSS board have been assembled, it is possible to burn the LCSS firmware on the board by using the "ICD2" programmer and the MPLAB IDE v. 8.66 distributed by Microchip (see https://www.microchip.com/development-tools/pic-and-dspic-downloads-archive (https://www.microchip.com/development-tools/pic-and-dspic-downloads-archive) ). The program to burn on the LCSS board microcontroller is the "lcss_adapter.hex", located in the subfolder "lcss_adapter/firmware". When the user is going to connect the programming cable to the J7 socket of the LCSS board, he has to be careful to insert the male connector correctly: pin n.1 of it has to be inserted in the pin n.1 of the J7 socket. All the files related to the LCSS firmware are available in the subfolder "lcss_adapter/firmware/project_files" for modifications. The code of the LCSS firmware is written in "C" language; PCH libraries distributed by CCS are required to modify and compile the source code (see: https://www.ccsinfo.com/product_info.php?products_id=PCH_full ).

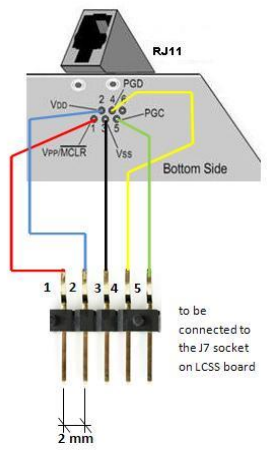
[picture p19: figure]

9

Figure 8: connections to make for assembling the cable to program the LCSS board.

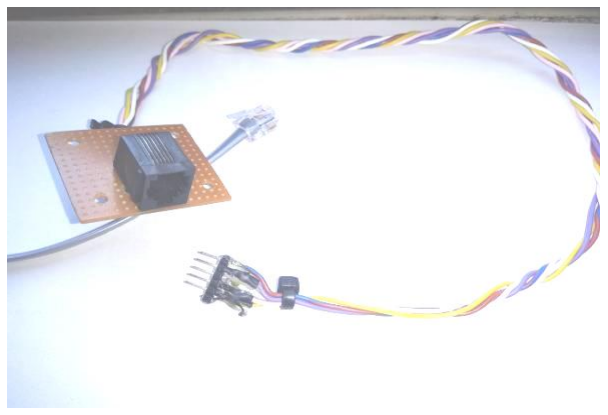
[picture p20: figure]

Figure 9: top view of the programmer cable for LCSS board.

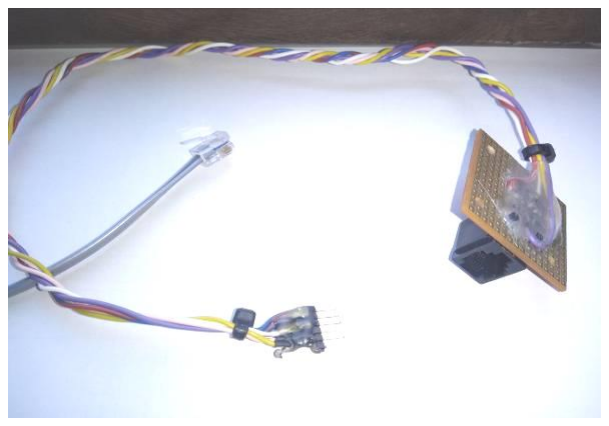
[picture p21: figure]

Figure 10: bottom view of the programmer cable for LCSS board.

## Using the ADC Pi

The second option for using analog output interface devices with SentinAir is given by mounting the ADC Pi board on SentinAir. This board is provided by ABelectronics (https://www.abelectronics.co.uk/) (see figure 11, 12) and it is based on the MCP3424 microprocessor, which is an analog-to-digital converter. The software driver for MCP3424, and therefore for the ADC Pi board, is already available in the repository of SentinAir in the folder “devices”. This board is featured by two MCP3424 microprocessors each containing four analog inputs. Therefore, the total number of signals for each ADC Pi board is eight. The maximum analog-to-digital conversion accuracy provided by MCP3424 is 17 bits. The

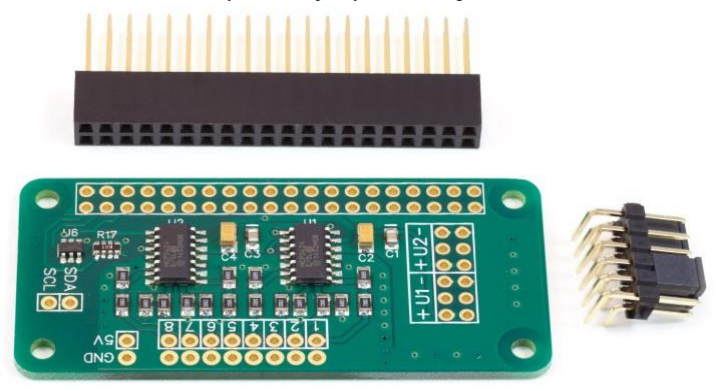
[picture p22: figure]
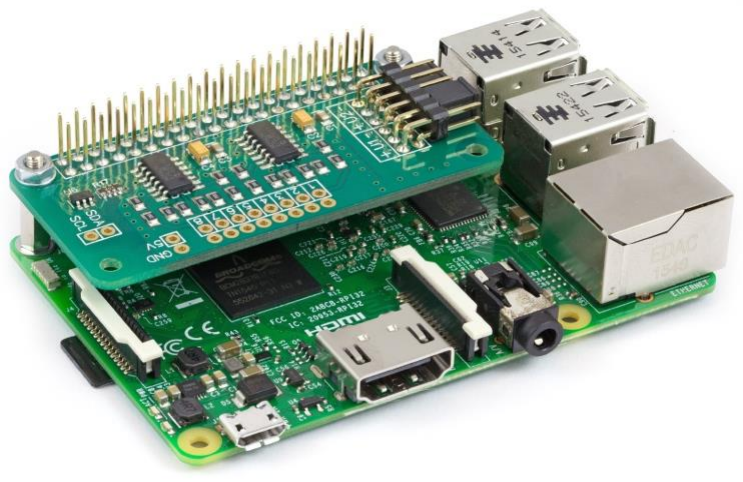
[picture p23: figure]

10

ADC Pi is attached to the Raspberry board through the Raspberry GPIO connector. This board is interfaced with the Raspberry through the I2C port. No electrical wiring is necessary to connect the ADC Pi board to Raspberry, because the power and the I2C bus connections are provided by the GPIO connector to insert directly on the Raspberry board (see figure 12).

Figure 11: ADC Pi board layout. The V1 and V2 terminals are devoted to the I2C address selection of the two MCP3424 microprocessors of the board. The jumpers of the connector on the right side of the picture set the I2c bus address of each microprocessor. The pins numbered from 1 to 10 are the analog inputs.

Figure 12: the ADC Pi connected to the Raspberry Pi through the GPIO connector.

11

## SentinAir software installation (basic procedure)

This is the quick procedure to install the SentinAir software making the minimum steps. If you desire a higher level of customization, you can refer to the “SentinAir software installation (advanced procedure)” chapter of this guide. The basic installation procedure is composed of two steps:
a) Installing the SentinAir sd card image
Download the latest SentinAir SD card image file. (https://drive.google.com/file/d/1KaBjFTMJjB79ryGpAMCCBvThq09m7BA6/view?usp=sharing) Flash it in an SD card having at least 2 GB (4 GB recommended) of memory space by using, for example, Win32diskimage.exe program (for Windows operative systems).
b) Enabling the use of the IMAP-SMTP module (optional)
To use the IMAP-SMTP module (see the chapters “SentinAir start up”, and “controlling SentinAir by e-mail”), please, follow the steps described in points 6 and 7 of the section “Installing the SentinAir software”.

### SentinAir start-up after the basic installation procedure

Supposing you have finished the a) point of the basic installation procedure, insert the SD card in the SentinAir device, plug one or more devices among the ones listed in table 1 into one of the system ports, and give power to SentinAir. After a few seconds, the green light starts blinking. Following this stage, the yellow light starts blinking. This means that the system is performing the port scanning. If one or more devices/sensors/instruments are found, the system automatically starts to acquire data (entering in the active monitoring mode and starting a new measurement session), and the yellow light turns on. To stop the measurement session, you have to use the “SentinAir user interface” and send the on-purpose command to the system (please, refer to the “Using the SentinAir user interface” chapter of this guide).

### SentinAir software installation (advanced procedure)

The procedure described below allows skilled users to customize the SentinAir system during the installation process. All the software necessary to operate a SentinAir device runs on Raspbian Stretch Lite Operative System (OS); therefore, the first step is downloading and installing it on a SentinAir device or a Raspberry 3 B+ board. For a correct SentinAir software installation, please, follow in sequence the below procedures. For the first software installation, the user has to plug a keyboard into the USB port and a monitor into the HDMI port. Optionally, it is possible to access the system via SSH connections by using programs such as putty.exe or WinSCP.exe (for Windows operative systems), but this procedure needs a keyboard and a monitor.
a) Installing Raspbian Stretch Lite operative system
1. Download the Raspbian Stretch Lite OS image (which file is “2018-06-27-raspbian-stretch-lite.zip”) into a computer from the link: https://downloads.raspberrypi.org/raspbian_lite/images/raspbian_lite-2018-06-29/ and flash it in an SD card memory featured by at least 2 GB of room by using, for example, Win32diskimage.exe program (for Windows operative systems).

12

2. Create a blank file called ssh (no extension). Save this file in the root of the MicroSD card with the flashed image. This operation is for enabling SSH connections at start-up.
b) Preparing Raspbian for SentinAir installation
1. Power the SentinAir device or the Raspberry 3 B+ board, log in it (the default user and pass are respectively: “pi” and “raspberry”), and type the command: sudo raspi-config.
2. To set the device name, select Network Options/Hostname and insert the device name. It is mandatory to enter a name with a "hyphen" inside, for example, sentinair-S1. This is for the correct functioning of SentinAir software. The part of the name following the hyphen is the identity number you choose for the device. Do not exit from raspi-config yet.
3. To use the serial port for connecting devices, select Interfacing options/Serial and then press in sequence "NO" and "YES". If everything is fine, you should see the message "The serial login shell is disabled. The serial interface is enabled". Then press "OK".
4. To use I2C ports for connecting devices, select Interfacing options and then P5 I2. Select “yes” to enable the I2C ports.
5. To expand the use of the memory on your SD card, select Advanced Options/ expand Filesystem. Select then FINISH and reboot the system.
6. Run the command sudo nano /etc/hosts and update the file by modifying the line: "127.0.0.1 raspberrypi" in the line: "127.0.0.1 <device-name>", where <device-name> has to be the same name selected in the step 2 (which is, as for example sentinair-S1). Reboot the system.
7. To complete the configuration for the serial port called /dev/ttyAMA0, we have to disable the Bluetooth service that uses this port and set it as a general-purpose serial port. To do this, type sudo nano /boot/config.txt, and then add at the end of the file, the row: dtoverlay=pi3-disable-bt. Save and close the file. After doing this, prevent Bluetooth service to use serial port by typing the command: sudo systemctl disable hciuart. Then reboot the system by running sudo reboot.
8. To enable the external green led for CPU activity, edit the file /boot/config.txt as done in the
step 7 and add the line: dtparam=act_led_gpio_19. Save, close the file, and reboot the system.
9. As the Stretch version of the operative system is no longer supported, it is necessary to modify the website of the repository by editing through the “nano” command, as earlier done, the file /etc/apt/sources.list. In this file you must substitute the line “deb http://raspbian.raspberrypi.org/raspbian/ stretch main contrib non-free rpi” with the line “deb http://legacy.raspbian.org/raspbian/ stretch main contrib non-free rpi”, then save and close the file
10.Make sure that your raspberry board is connected to internet through a wired connection or via a USB stick modem with a valid SIM card enabled by an Internet Service Provider to connect to the Internet (for example, the model Huawey E303 does not require installation procedures). This is necessary because the built-in Wi-Fi modem will turn in a Wi-Fi access point, and therefore it is impossible to continue while SentinAir is connected to a pre-existing Wi-Fi LAN. Update the Raspbian repository by typing the command: sudo apt-get update.
11. Download and install dnsmasq and hostapd by typing the command sudo apt-get install -y dnsmasq hostapd.

13

12. Stop the execution of the software just installed by running the commands: sudo systemctl stop dnsmasq and sudo systemctl stop hostapd
13. Set a static IP for the system and configure dhcpcd by opening the file dhcpcd.conf with the command sudo nano /etc/dhcpcd.conf and add at the end of the file the lines:
interface wlan0
static ip_address=192.168.4.1/24 (or an alternative IP address you choose)
nohook wpa_supplicant
dhcp-range=192.168.4.2,192.168.4.100,255.255.255.0,24h
Save and close the file.
14. Configure the hostapd software by creating the file hostapd.conf , to do this, run the command sudo nano /etc/hostapd/hostapd.conf . Then insert in the file the following lines: interface=wlan0
driver=nl80211
ssid=device-name (for example: sentinair-S1)
hw_mode=g
channel=7
wmm_enabled=0
macaddr_acl=0
auth_algs=1
ignore_broadcast_ssid=0
wpa=2
wpa_passphrase=sentinair1
wpa_key_mgmt=WPA-PSK
wpa_pairwise=TKIP
rsn_pairwise=CCMP
Then save and close the file.
15. Complete hostapd configuration by typing sudo nano /etc/default/hostapd. Then modify the line:
#DAEMON_CONF=””

in the new line
DAEMON_CONF=”/etc/hostapd/hostapd.conf “
Save and close the file.
16. Run the command sudo nano /etc/init.d/hoastapd and replace the line DAEMON_CONF=
whit the line
DAEMON_CONF=/etc/hostapd/hostapd.conf.
Save and close the file.
17. Run the command sudo nano /etc/dnsmasq.conf and add at the end of the file the following lines:
interface=wlan0
dhcp-range=192.168.4.2,192.168.4.100,255.255.255.0,24h.
Save and close the file.
18. Finally, run the commands:

14

sudo systemctl restart dhcpcd. sudo systemctl unmask hostapd sudo systemctl enable hostapd sudo systemctl start hostapd
sudo service dnsmasq start
sudo reboot
c) Installing the Python libraries
1. Install python3-serial by running the command sudo apt-get install python3-serial.
2. Install the library RPi.GPIO by running the command sudo apt-get install python3-RPi.GPIO.
3. Install the library Pandas by running the command: apt-get install –y python3-pandas
4. Install the library python3-matplotlib by running the command sudo apt-get install python3-matplotlib
5. Install pip3 by running the command sudo apt-get install python3-pip
6. Install the library libscrc by running the command sudo pip3 install libscrc.
7. Install the library smbus2 (for i2c managing) by typing the command sudo pip3 install smbus2
8. Reboot the system.
d) Installing the SentinAir software
1. Create the folder /home/pi/sentinair. SentinAir software files have to be mandatorily copied into this folder
2. Copy in /home/pi/sentinair/ the following files:
- sentinair.py
- sentinair_system_manager.py
- sentinair_system_installer.py
- imap-smtp-interface.py
- imap-smtp-monitor.sh
- mail-config.sentinair
- pass
- favicon.ico
3. In the directory “home/pi/sentinair”, create the directories:
a. “devices”
b. “img”
c. “logs”
d. “data”
e. “avg”
f. “plots”
4. Copy in the directory “img” the following files:
a. “sentinair.png”
b. “btnplt.png”
c. “havg.png”

15

d. “davg.png”
e. “conf.png”
f. “stop.png”
g. “scan.png”
h. “confirmpurge.png”
i. “cancelpurge.png”
j. “purge.png”
k. “file_not_found.png”
5. Copy in the directory “devices” the following files:
a. “__init__.py”
b. “ac32.py”
c. “af22.py”
d. “bh1750.py”
e. “bme280.py”
f. “co12m.py”
g. “go3.py”
h. “irca1.py”
i. “lcss_adapter.py”
j. “mcp342x.py”
k. “mhz19.py”
l. “multisensory_board.py”
m. “nox405.py”
n. “o342.py”
o. “pms5003.py”
p. “pms3003.py”
q. “sps30.py”
r. “v72m.py”
6. In order to get started SentinAir software when the system boots, insert the following lines in the file /etc/rc.local before the line “exit 0”:
python3 /home/pi/sentinair/sentinair_system_manager.py&
WARNING: if you are editing rc.local on a Windows OS, remember to convert it in Unix/Linux format through the “dos2unix.exe” utility.
7. Open the “mail-config.sentinair” file and put your e-mail account data in the lines without the comment character (#) avoiding inserting the “space” character, like the example below: MAIL_ADDRESS="my-email_address@my_company.com" MAIL_PWD="my-email-account-password"
SMTP_SERVER="my-smtp-server-url"
IMAP_SERVER="my-imap-server-url"
8. Reboot the system

16

### Setting up SentinAir internet wireless connection

The USB stick modem Internet plugged into one of the USB ports available gives a way to reach a SentinAir system from the internet. If a Huawey E303 is used for the purpose, no installation procedures are required. Other USB stick modem models have not been tested yet. Internet Service Providers (ISP) usually do not give public IP addresses to the user; therefore, SentinAir could not be reachable from anywhere. To overcome this issue, it is possible to use the "IP tunneling" services that give the possibility to get around this hurdle. Prices of these services can vary from free to a few Euros per month. Examples of web companies offering these services are www.dataplicity.com, or www.pitunnel.com or. https:\\remote.it.

### SentinAir start-up

SentinAir gets started when the electronic hardware is powered, alternatively, by typing the command: sudo python3 /home/pi/sentinair/sentinair_system_manager.py. After few seconds the system is powered, you should see the green light asynchronous blinking, which indicates that the CPU is exchanging data with the SD memory and the system is setting up (see table 3).

Table 3: check light behaviors and their meaning
LED | LED STATUS | MEANING
RED | OFF | System turned off
| BLINKING | Sensor fault (the user must see the log file to get more information)
GREEN | ASYNCHRONOUS BLINKING | Data exchange activity between CPU and SD memory
YELLOW | OFF | System active, monitoring not active
| FAST BLINKING | The system is performing the port scanning to find which devices are connected
| SLOW BLINKING | The shut-down procedure is going on, following the shut-down button pressing
| ON | Monitoring active

When SentinAir gets started, before getting ready, it performs some preliminary operations to work appropriately. Firstly, it makes blink the yellow check light to indicate that the system is performing the scanning of the system ports to find which devices, among the ones whose driver is already installed in the system, are plugged into. When a device is found, it got connected to the system. This operation might last a few seconds, and during this time, you should see if you have a monitor plugged into the HDMI port, system messages on the screen. From now on, all the relevant operations and events are logged in the on-purpose log file of the system manager (the default name is sentinair-log.txt). During this period, the system cannot accept commands from the user; sometimes, it can last a few minutes. As soon as this operation is completed, SentinAir reads the file status.sentinair, where there is information about the device status: "standby", or "active monitoring". If the system is in "active monitoring" status, a new measurement session gets started; therefore, the yellow led check light turns on, and a new file containing the measurement data is created. The last operation of the start-up phase is the sending of an e-mail to the e-mail address indicated in the file mail-config.sentinair if the USB stick modem is plugged into the system (see figure 14). In the current version of the software, SentinAir configuration is featured by a static IP on the cable Ethernet port. Devices connected to this interface will form a "stand-alone" net that is

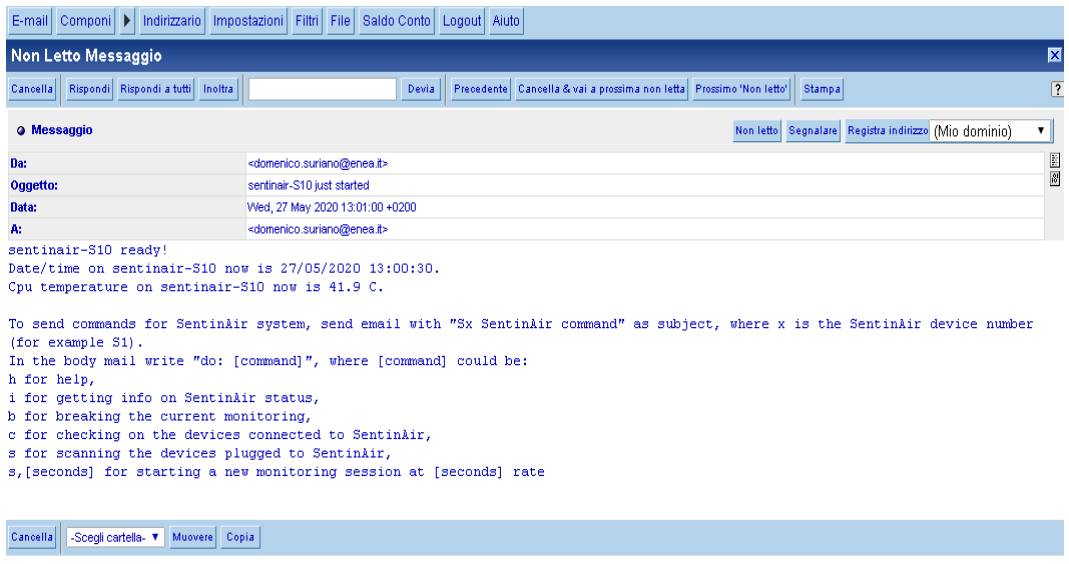
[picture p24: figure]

17

not connected to the Internet. If the user needs to connect more devices, for example, it is possible to use an Ethernet switch.

Figure 14: E-mail sent by SentinAir at start-up time.

### Installing devices drivers in SentinAir

SentinAir can read data from any device as long as the specific driver of the device is installed in the system. It is mandatory that the device driver files have to be in the folder /home/pi/sentinair/device. In order to easily install drivers, the user can log into the system by SSH connection via the Wi-Fi link through the LAN set up by SentinAir. Then the user has to use the module sentinair_system_installer.py by opening it through the command:
sudo python3 /home/pi/sentinair/sentinair_system_installer.py.
Once opened the installer, the commands available are listed in table 4.

Table 4: commands available for the SentinAir system installer
Command function | Command syntax | Example | Effect
Device driver installation | i,device_name.py | i,pms3003.py | Installs the driver for the device pms3003
Device driver uninstalling | u,device_name.py | u,pms3003.py | Uninstalls the driver for the device pms3003
Checking the current drivers installed | c | c | Displays a list of the drivers currently installed
Modifying the current path of the system manager module | m | m | Writes in the file "manager_dir.sentinair" the new path of the manager system module

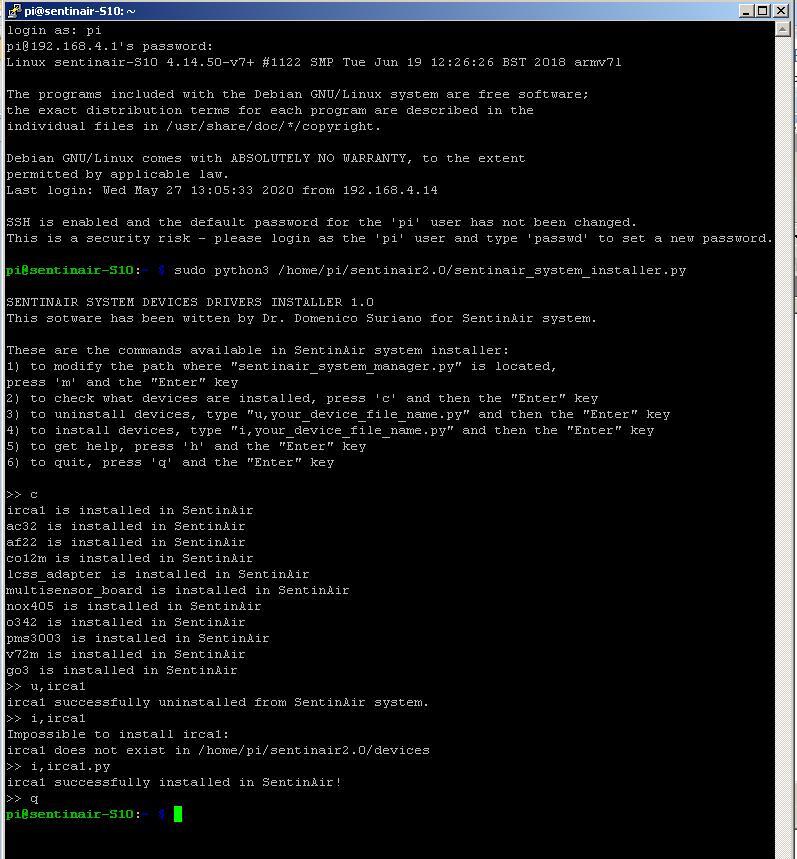
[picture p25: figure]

18

Asking for the commands list available | h | h | Displays a brief manual where are shown the commands
Quit the program | q | q | Quits the programs

An example of sentinair_system_installer.py use is shown in figure 15. After updating the system with new installations, it has to be rebooted or restarted.

Figure 15: the installer user interface

19

### Using the SentinAir user command line interface

SentinAir system main interface is provided by the sentinair.py module. The user has to log into the system by SSH connection via the Wi-Fi link through the LAN set up by SentinAir. To open the SentinAir user interface, type the command:
python3 /home/pi/sentinair/sentinair.py.
Once opened the user interface, the commands available are listed in table 5.

Table 5: commands available for the SentinAir user interface
Command function | Command syntax | Example | Effect
Starting a new monitoring session | s,seconds | s,60 | A new monitoring session gets started. Every 60 seconds, device measurements data are read and stored in a file
Stopping a measurement session | b | b | Stops the current measurement session
Retrieving information about the system status | i | i | Displays information such as the devices currently connected to the system, the sampling rate of the measurement session, or if the system is on standby.
Retrieving information about the devices connected to the system | c | c | The system returns the information about the connected devices: identity, units of measurements, current measurements
Asking for the commands list available | h | h | Displays a brief manual where are shown the commands
Scanning the ports and connecting the devices plugged into SentinAir ports | s | s | The system scans all the ports (USB, Ethernet, etc.) and recognizes if one of the installed devices is plugged into
Quit the program | q | q | Quits the programs

An example of the use of the SentinAir user interface is shown in figure 16. If the system is not in active monitoring mode (you can see this by checking the yellow light, which should be off), the message “No measurement session ongoing” is shown. If you want to start acquiring data from sensors (putting the system in active monitoring mode), you have to type the command “s,60”. This way a monitoring session will start at 60 second sampling rate and the yellow check light will turn on.

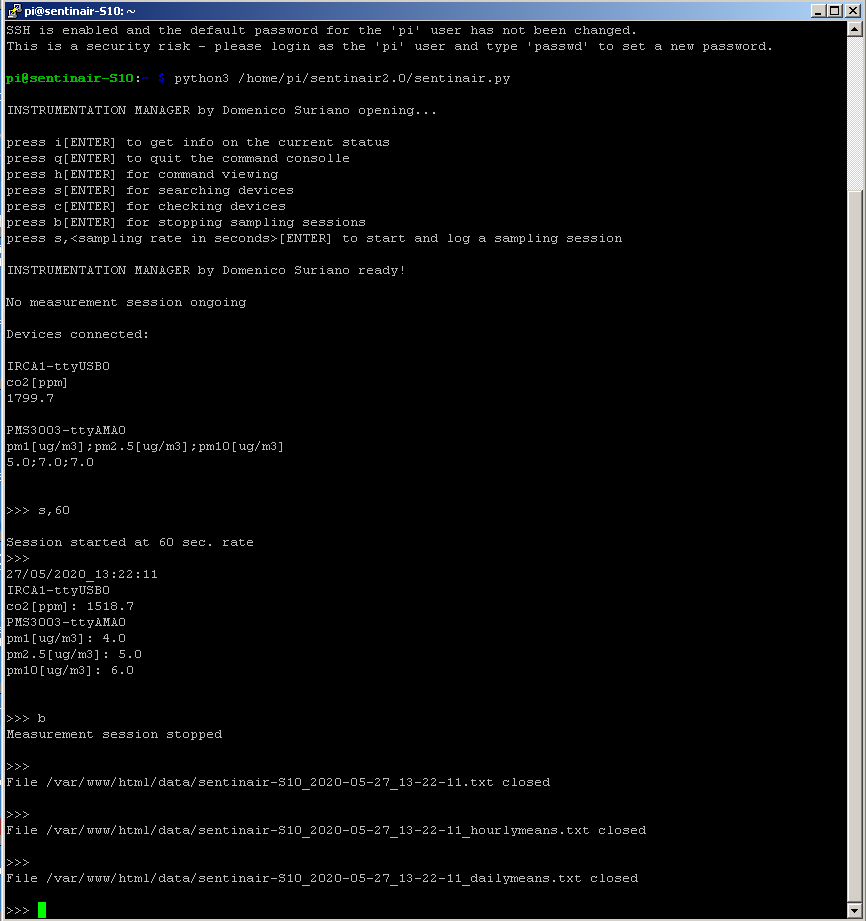
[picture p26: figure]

20

Figure 16: the SentinAir user interface.

### Setting SentinAir system date and time

SentinAir system has not a hardware Real Time Clock (RTC). If the device is connected to internet, it automatically updates date and time of the system, otherwise, if necessary, the user must update manually it. To carry out this operation, no measurement session must be active; in this case, before setting correct date and time, the user must stop the current measurement session by opening the SentinAir user interface and by typing the command “b” (see table 5). Once done this operation, the user must quit the program by launcing the “q” command (see table 5), and subsequently, he can set the current date and time by running the Linux command “date” as follows: “sudo date –s=”YYYY-mm-dd hh:mm:ss”. For example, if you want to set the date and time on the 23th of February 2022 at 23:44:21, you must type the command: “sudo date –s=”2022-02-23 23:44:21”. Stopping the measurements and setting the new date/time system can be done optionally by using the web pages

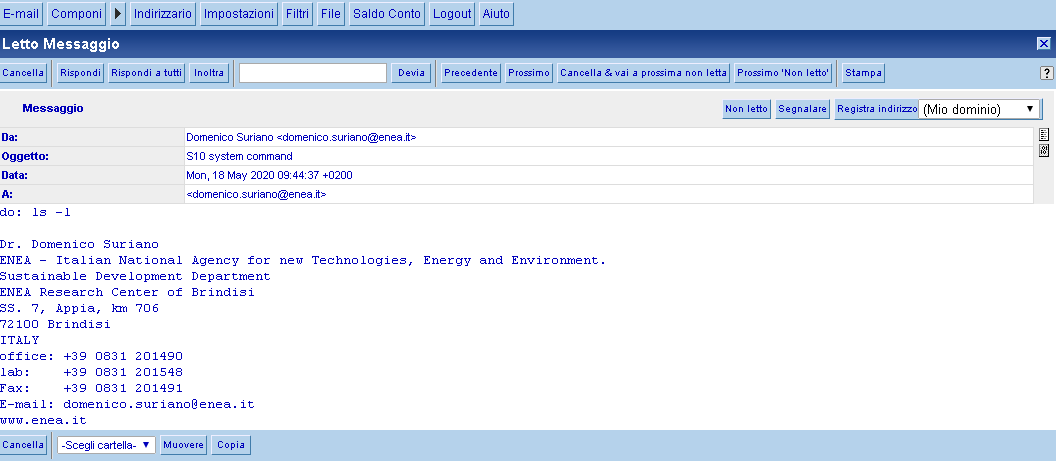
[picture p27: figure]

21

which offer a graphical user interface for the system control (in this case, refer to the chapter “SentinAir web pages”).

### Controlling SentinAir by e-mail

SentinAir has been designed for being used in all that cases where it is necessary to perform experiments or measurements in remote areas, where possibly the internet link is weak or unstable, and therefore, where it is difficult the remote control and the data download from the device. For this purpose, commands and data can be exchanged by e-mail sending and receiving. SentinAir checks periodically on the IMAP server configured in the imap-smtp-interface.py for the presence of e-mails containing commands, and when the radio signal allows it, sends back the response. The imap-smtp-interface.py module is optional, and it is not essential for SentinAir operation. If it is present, it is launched by sentinair_system_manager.py at start-up. The user can send commands through e-mail for both the SentinAir system or for the operative system programs and services. A typical SentinAir command is, for example, "s,60", which causes the start of a new measurement session at 60 seconds sampling rate. A command directed for the operative system could be, for example, "ls –l", which returns the list of files and directories contained in the current system directory. E-mails containing commands for the operative system must have as subject the text: "device_ID system command",
where the "device_ID" is the part of the device name which follows the hyphen. For example: if the device name was set as "sentinair-S1" during the software installation process, then the device_ID will be "S1" (see figure 17 and 18). Moreover, e-mails containing commands directed to SentinAir software must have as subject the text:
"device_ID SentinAir command" (please, mind the correct case of letters).
The body of the e-mail must have a line where there is "do: command". For example: "do: s,60" (please, mind the "space" character between "do:" and the command). It is possible to download every kind of file present in the device by sending an e-mail having the subject as: "device_ID system command", and the body having the line as: "do: fget /path_of_the_file/file_to_download" (mind the space characters between "do:" and "fget" and between "fget" and "/path_of_the_file/file_to_download"). For example: "do: fget /var/www/html/log/sentinair-log.txt".

Figure 17: e-mail sent to SentinAir containing a command for the operative system

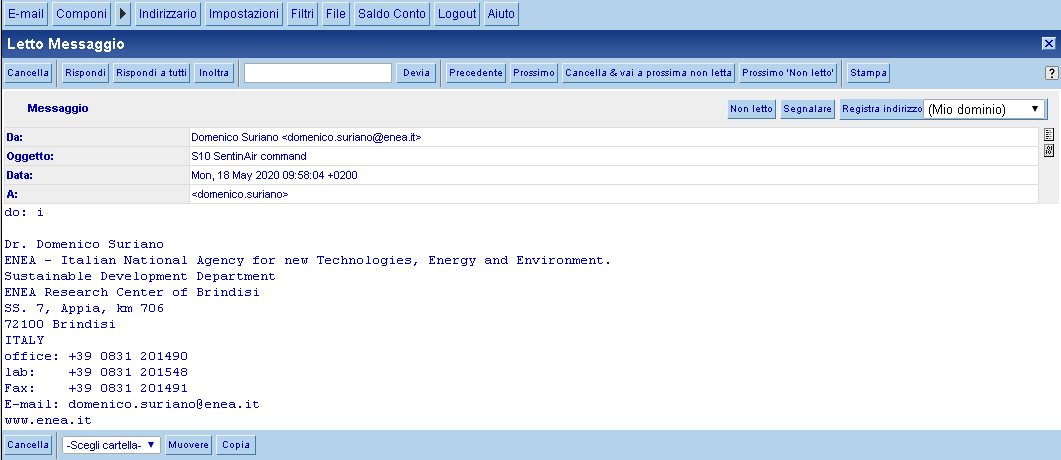
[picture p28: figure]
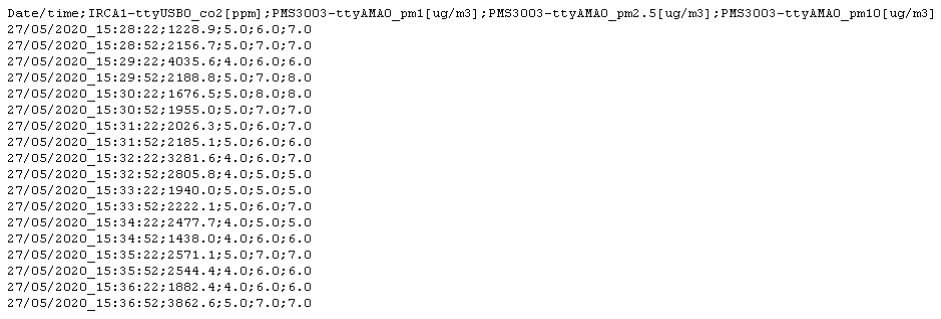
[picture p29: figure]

22

Figure 18: -mail sent to SentinAir containing a command for SentinAir system

### SentinAir operations featuring the measurement session

When a new measurement session gets started (for example, by the command "s,60"), the yellow led check light turns on. Three new files are created: the file containing the records of the measurements along with the timestamps (see figure 19) and named: "device_name_date_time.txt" (for example sentinair-S1_2020-02-03_09-30-15.txt), the file containing hourly averages of measurement and named: "device_name_date_time_hourlymeans.txt" (for example: "sentinair-S1_2020-02-03_09-30-15_hourlymeans.txt"), and the file containing the daily averages of the measurements, named: "device_name_date_time_dailymeans.txt" (for example: "sentinair-S1_2020-02-03_09-30-15_dailymeans.txt"). Hourly and daily averages are computed in real-time by the module sentinair_system_manager.py, and they are stored in the path indicated in that module (which is for default: "/var/www/html/data"). Another operation performed by the sentinair_system_manager.py module during the measurement session is the plotting of each magnitude measured by each of the devices connected to SentinAir. The plots are stored in jpg files placed in the path "/var/www/html/img" (which is their default path). Those files are encapsulated in web pages and served to the user when he connects by a web browser to SentinAir.

Figure 19: a file containing records of a SentinAir measurement session.

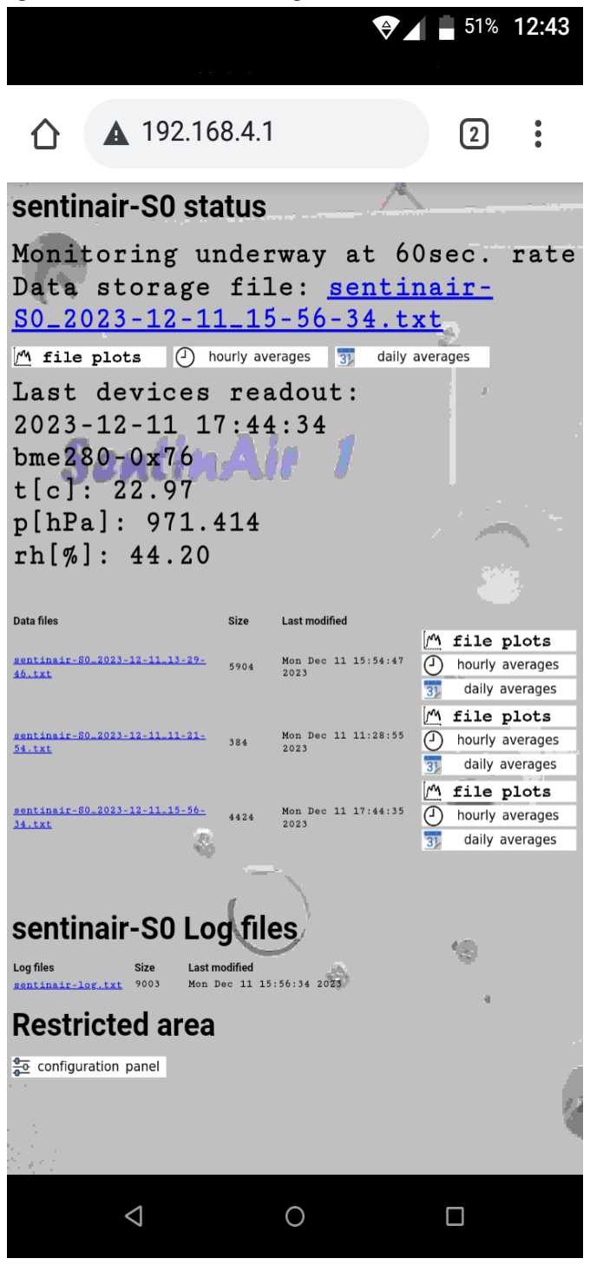
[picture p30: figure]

23

### SentinAir web pages

The user can control SentinAir activity by connecting through a web browser to SentinAir (see figure 20). As for the other user interfaces given by the sentinair.py module and the sentinair_system_installer.py module, the webserver of SentinAir can be reached by connecting through a Wi-Fi link at the address set in in the installation procedure (which default is 192.168.4.1), or through internet connections via the selected "IP tunneling" service. Web pages of SentinAir allow the user to perform all the tasks that are carried out by the command line interface. Therefore, they represent a second way to control and monitor the system. The main page is represented by the status page of SentinAir (see figure 20).

Figure 20: status web page of SentinAir

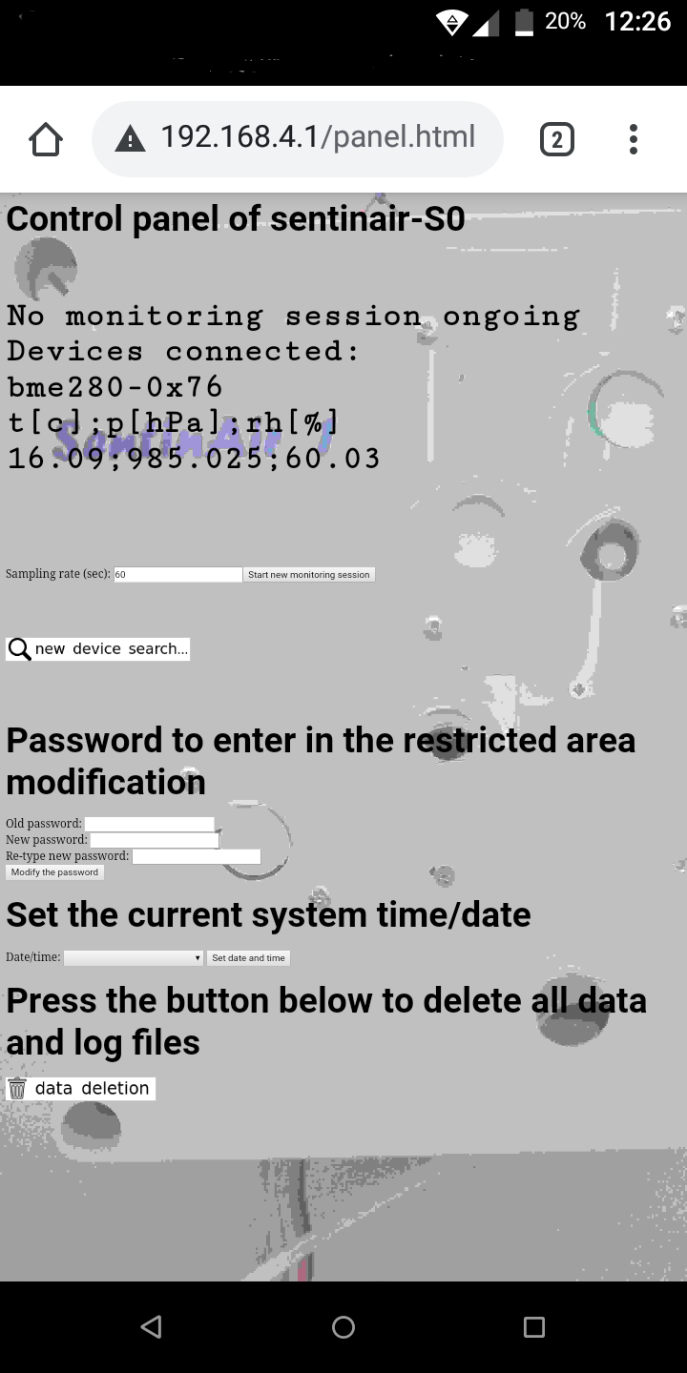
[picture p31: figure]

24

The button called “file plots” allows to plot the data present in the related file, while the “hourly averages” and the “daily average” buttons allow respectively to generate and plot hourly and daily averages of the related files. The button called “configuration panel” offers the way to access to the restricted web area from where the user can carry out all the operations which typically are performed thorough the command line interface in addition to other operations. The default user and password to get access to the restricted area are respectively “sentinair” and “sentinair1”. Once the user has got access in the restricted area, he can modify the password as he prefers. Through the pages composing the restricted web area (see figure 21), the users can perform the operations listed in table 5 and they also can safely cancel the files related to the old data and purging the log file. The installation or uninstallation of new devices or sensors must be carried out by using the command line interface called “sentinair_system_installer.py” as explained in the chapter “Installing devices drivers in SentinAir”.

Figure 21: one of the web pages composing the restricted web area

25

### Shutting down SentinAir

To shut down the system through the button shown in figure 4, the user has to press it and hold it pressed until the yellow light starts blinking. At that moment, it is possible to release the button. Before taking off the power from the system, you have to wait that the yellow light stops blinking and after that, wait the green light stops blinking and the red light turns off. Optionally, you have to type the “sudo halt” command to the operative system running on the Raspberry board to properly shut-down the system.

### How to write device drivers for SentinAir

The creation of new device drivers for SentinAir is highly expected. It is desirable that researchers, or users, write drivers for their own devices to use with the SentinAir system. In order to facilitate this task, driver templates have been written and stored in the folder “devices/device-driver-templates” of the SentinAir Github repository. (https://github.com/domenico-suriano/SentinAir) When a new driver is going to be written, the user must follow some rules in order to get it fully compatible and operating with the pre-existing software. Some of these rules are common to all types of devices (USB, serial, I2C, Ethernet), while there are rules specific for each type of sensor/device. We recall that sensors or devices featured by analog output interfaces must be used with the LCSS adapter board (having a USB output interface), or with the ADC Pi (having an I2C output interface). A good way to getting started with writing new device drivers is by modifying the template file related to your device type (“ethernet-device-template.py”, “usb-device-template.py”, “serial-device-template.py”, or “i2c-device-template.py”).
Here below it is shown a step by step procedure which hopefully will help the user to correctly write new device drivers. In doing this, we will report some examples referring to the files of some drivers already developed (“nox405.py”, ” ac32.py”, ”bh1750.py”), and to the files of the driver templates.
1. Import the necessary library. For I2C devices, “smsbus2” is mandatory (see “bh1750.py” and “i2c-device-template.py”), for USB and serial devices “serial” is mandatory (see “nox405.py” and “serial-device-template.py”), for Ethernet devices “socket” is mandatory (see ” ac32.py” and “ethernet-device-template.py”). Also import other libraries specific for your device operation (see for example “time” and “_thread” in “nox405.py”)
2. Set the mandatory constant strings CONNECTION_TYPE, DEVICE_IDENTITY, and DEVICE_SENSORS common for all the device types following the indications in the driver template files (“ethernet-device-template.py”, “usb-device-template.py”, “serial-device-template.py”, or “i2c-device-template.py”). The DEVICE_SENSORS string contains the magnitude names measured by the device, separated by a semicolon character; for example (see “nox405.py”): "no2[ppb];no[ppb];nox[ppb]". Then set the constants specific for each type of device: I2C_ADDRESSES, which must be a Python list of integer values (for I2C devices, see “bh1750.py” and “i2c-device-template.py”), ETH_ADDRESSES, which must be a list of strings (for Ethernet devices, see ” ac32.py” and “ethernet-device-template.py”), DEVICE_BAUD_RATE, which must be an integer value (for serial and usb devices, see “nox405.py” and “serial-device-template.py”). Set the other constants (if any) specific for your device operation.

26

3. Create the device class name. It is mandatory that the class name must be the same as the driver file name with the first letter capitalized. For example: the driver “nox405.py” contains the class Nox405.
4. In the “__init(self)” method of the device class, you can find the mandatory variables common for all the device types:
self.identity = DEVICE_IDENTITY
self.connection_type = CONNECTION_TYPE
self.sensors = DEVICE_SENSORS.
There are also variables specific for a device type. For I2C device (see “bh1750.py” and “i2c-device-template.py”), you will find:
self.addresses = I2C_ADDRESSES
self.device_address = 0x00.
For Ethernet devices you will find (see ” ac32.py” and “ethernet-device-template.py”): self.addresses = ETH_ADDRESSES
self.device_address = None
self.sk = None
For serial or usb devices you will find (see “nox405.py” and “serial-device-template.py”): self.baud_rate = DEVICE_BAUD_RATE
self.portname = ""
self.port = None.
The user must not modify the above-mentioned lines, but he can add variables necessary and specific for his device operation (see, for example, the “__init(self)” method in the file “nox405.py”).
5. The device class must contain the following methods common for all the device types; they are:
def getConnectionType(self):
return self.connection_type def getIdentity(self):
return self.identity
def getSensors(self):
return self.sensors
def setIdentity(self,idstring):
self.identity = idstring
Moreover, for a specific device type, there are other mandatory methods. For I2C devices device (see “bh1750.py” and “i2c-device-template.py”), we have:
def getConnectionParams(self):
return self.addresses
def terminate(self):
self.device_address = 0x00.
For Ethernet devices (see ” ac32.py” and “ethernet-device-template.py”), we have: def getConnectionParams(self):
return self.addresses
def terminate(self):

27

try:
self.sk.close()
except:
return
def __del__(self):
try:
self.sk.close()
except:
return
For usb or serial devices (see “nox405.py” and “serial-device-template.py”), we have: def getConnectionParams(self):
return [self.portname,self.baud_rate]
def terminate(self):
try:
self.port.close()
except:
return
def __del__(self):
try:
self.port.close()
except:
return.
The user must not modify the above-listed methods, but he can add other ones specific for his device operation (see, for example, the “nox405.py”, ” ac32.py”, “bh1750.py”).
6. The class must have the method called “connect(self,address)” in case of I2C or Ethernet devices, or “connect(self,portname)” in case of serial or usb devices. This method detects if the device is connected and finds the connection parameters, for example, if it is searching for an Ethernet or I2C device, it finds the device address; or, if it is searching for a USB or serial device, it finds the USB port. If no device is found, it returns the "0" value, otherwise, it returns "1". For implementing the "connect" method, I suggest to request data from the device and see if it responds. If this operation succeeds, it means that the device is correctly connected, and in this case, the 1 value will be returned (see, for example, the “nox405.py”, ” ac32.py”, “bh1750.py”).
7. The device class must have the method "sample(self)" that must return a string containing the last measurements separated by a semicolon mark. An example of a string returned by this method could be: “27,76;0,1234;456,9”. It is mandatory that the fields contained in the string must be in the same number as the ones set in the DEVICE_SENSORS string. For example: if DEVICE_SENSORS=“no2[ppb];no[ppb];nox[ppb]” (see “nox405.py”), then the "sample(self)" method must return “27,76;0,1234;456,9".

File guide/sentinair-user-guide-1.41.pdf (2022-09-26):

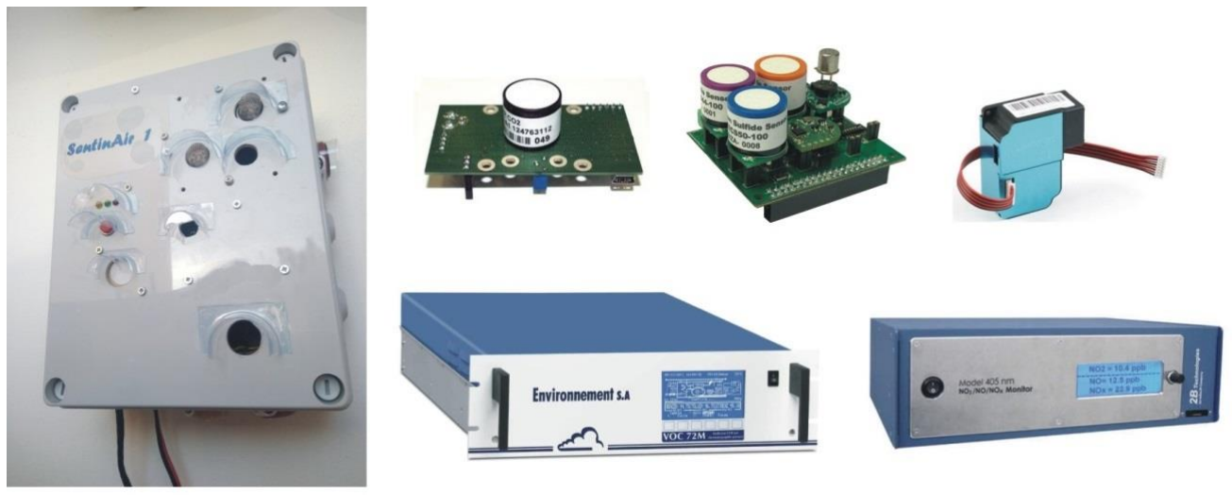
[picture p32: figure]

1

User Guide

Project designer and developer

Dr. Domenico Suriano, (https://materiali.sostenibilita.enea.it/people/domenico-suriano) domenico.suriano@enea.it

This user guide version (v. 1.41) refers to the SentinAir system version 1.4 available at the Github SentinAir repository. (https://github.com/domenico-suriano/SentinAir)

Description

SentinAir is a device designed and developed for data acquisition from diverse types of instruments, sensors, or devices (see figure 1). The core of the system is the Raspberry 3 B+ board; therefore, the software presented in this guide can be installed either on a SentinAir device or a Raspberry 3 B+ board. Devices have to be plugged into SentinAir by USB, Ethernet, serial UART, SPI, or I2C port. Currently, the system has been tested only with devices connected by the USB, I2C, Ethernet, and serial UART port available on the Raspberry board, which is the "brain" of SentinAir. The system is based on command line interfaces, except for the web pages served by the webserver installed inside.

Figure 1: on the left, SentinAir device. On the right, some devices currently tested by SentinAir.

2

The system automatically recognizes the devices or instruments plugged into SentinAir through their specific driver, written in Python. The drivers currently developed are listed in table 1.

Table 1: device drivers developed currently for SentinAir and available in the github repository.
Sensor or device | Device driver | Connection interface | Supplier or manufacturer
BME280 (atmospheric pressure, temperature, and relative humidity) | bme280.py | I2C | Bosch Sensortec
BH1750 (luxmeter) | bh1750.py | I2C | ROHM semiconductor
MCP342x on ADC Pi board (to use devices having analog output signals) | mcp342x.py | I2C | Microchip
IRC-A1 (CO2 sensor) | irca1.py | USB | Alphasense
PMS3003 (PM sensor) | pms3003.py | TTL serial port | Plantower
PMS5003 (PM sensor) | pms5003.py | TTL serial port | Plantower
SPS30 (PM ssensor) | sps30.py | TTL serial port | Sensirion
MHZ19 (CO2 sensor) | mhz19.py | TTL serial port | Winsen
Multisensor board (to use devices having analog output signals) | multisensor_board.py | USB | Tecnosens
106L GO3 PRO package (CO2 and O3 monitor) | go3.py | USB | 2B technologies
405nm (NOx monitor) | nox405.py | USB | 2B technologies
LCSS USB adapter (to use devices having analog output signals) | lcss_adapter.py | USB | Designed and built in our lab
CO12M (CO chemical analyzer) | co12m.py | Ethernet port | Environnement
AF22M (SO2 chemical analyzer) | af22.py | Ethernet port | Environnement
AC32M (NOx chemical analyzer) | ac32.py | Ethernet port | Environnement
O342M (O3 chemical analyzer) | o342.py | Ethernet port | Environnement
VOC72M (VOC chemical analyzer) | v72m.py | Ethernet port | Environnement

SentinAir hardware
SentinAir is a modular and flexible system. The system hardware can be assembled in a minimal (see figure 2), or a typical configuration (see figure 3). The minimal hardware is composed of:
- a Raspberry 3 B+ board
- a class 10 SD card featured by a memory capacity of at least 2 GB (4 GB recommended),.
- a 5V power source capable of providing a direct current of 3A maximum. At the moment, the system has been tested with a switching ac/dc adapter (see figure 2).

The minimal configuration allows the user to use sensors/devices/instruments featured by a USB, serial UART, I2C, or Ethernet output interface, while analog output interfaces devices must be used with one of the analog-to-digital converter boards featuring the SentinAir typical hardware configuration. Ethernet or USB devices must be connected through the Ethernet and USB sockets

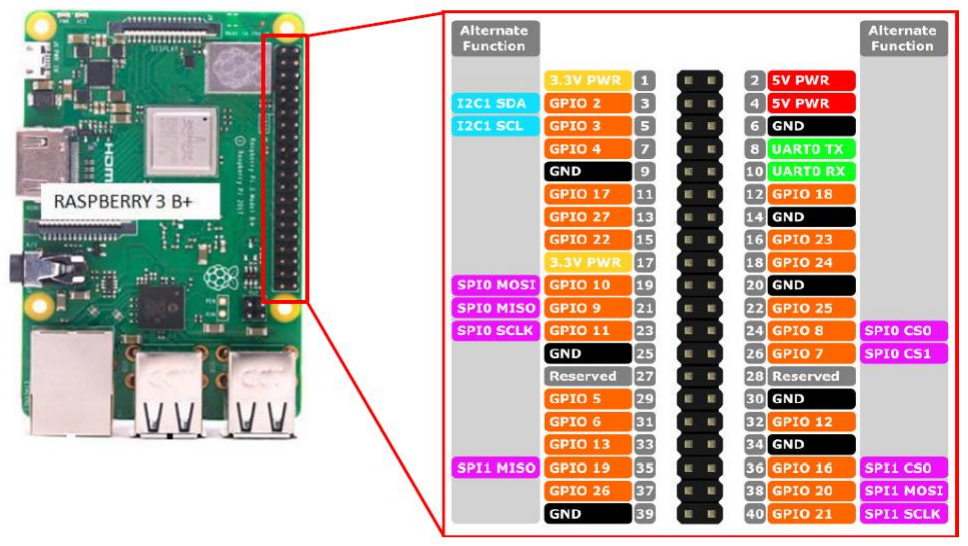
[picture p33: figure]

3

(see figure 2), while I2C and serial devices must be connected to the Raspberry GPIO connector following the indications of figure 3.

Figure 2: SentinAir hardware minimal configuration. Sensors/devices/instruments can be attached through the USB, Ethernet, Serial UART, or I2C port.

Figure 3: GPIO connector pinout. I2C devices to be used with SentinAir must connect their output to pins 3 and 5 (which is the I2C bus input). Devices having serial UART output must be connected to pins 8, 10. They can be powered through pin 2 or 4, if they need 5 Volts, otherwise, through pins 1, or 17. Device ground pins must be connected to one of the following pins: 6,9,14,20,25,30,34,39.

4

The typical hardware configuration of a SentinAir system is shown in figure 4, and it is composed of:
- A Raspberry 3 B+ board,
- a class 10 SD card featured with a memory capacity of at least 2 GB (4GB recommended),
- The check light system made of three LEDs and three 120 Ohm resistors. They are going to indicate the three possible states of the device: standby (yellow LED off), active monitoring (yellow LED on), and fault (red LED blinking),
- A push-button to properly shut down the whole system,
- A USB stick modem (the system has been tested with a Huawei E303),
- The expansion board, which is necessary to enable the simultaneous multiple connections of sensors. This board is provided by header pin connectors through which devices can be wired for the power supply or I2C bus interfacing. Three header pin connector rows provide 5, 3,3 Volts power supply, and ground connections; in addition to them, the other two pin rows offer a quick way to connect the devices SCL and the SDA signal to the mainboard I2C bus (see figure 4).
- An analog-to-digital converter board capable of giving output data on the USB, I2C, or Ethernet port. This board is necessary to convert analog outputs of sensors into digital data. In fact, the Raspberry board, on which the SentinAir system is based, has not got a built-in analog-to-digital converter; therefore, without it, the use of sensors/devices having analog output interfaces could not be possible. The user can use for this purpose any board that requires a power of 5 V and 0,2 A maximum. For example, the ADC Pi board based on the MCP3424 microprocessor by Microchip and supplied by ABelectronics (https://www.abelectronics.co.uk/) can fit the purpose. Another option is given by the LCSS adapter board (LCSS stands for Low-Cost Small commercial gas Sensors), which has been designed and developed to make the analog-to-digital conversion in an optimum way. The LCSS adapter board has been designed to minimize as much as possible the effects of the additional unwanted electronic noise, which may affect the conversion. Moreover, it has a 16-bit analog-to-digital converter that ensures a high resolution.


5

Figure 4: SentinAir hardware typical configuration. It includes an analog-to-digital converter board which enables the use of devices/sensors having analog output interfaces. This board can be the LCSS adapter or the ADC Pi by ABelectronics.

LCSS adapter assembly and setup
The LCSS adapter board allows the use of devices having analog output interfaces, and it is powered through its USB port. It converts the input analog signals into digital data that are given as output through the USB port. The analog outputs of the devices to be used with the LCSS adapter have to be wired to the J22 connector of the LCSS board (pins 4 to 11, see figure 6). These signals must be in the range 0 - 3,3 Volts. The LCSS adapter has a built-in temperature and relative humidity sensor. Eight analog-to-digital (ADC) converters feature it. They are high resolution (16 bits) converters, each of them having a signal amplifier and electronic noise filter. The user can set

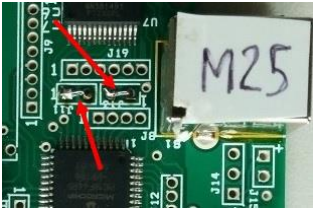
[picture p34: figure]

6

the gain of each amplifier through the resistive trimmers R14, R15, R23, R22, R30, R31, R38, R39 placed on the LCSS board (see figure 6). LCSS board can be used with the RN42XV Bluetooth adapter, even though its use is not necessary for the SentinAir system. The LCSS board is also designed to be used with rechargeable Li-Ion batteries. They have to be wired to the J15 connector (see figure 5), and they are automatically charged through the USB port. The use of batteries is not necessary for the SentinAir system.
Printed Circuit Board (PCB) files for LCSS assembly and setup can be found in the folder "lcss adapter". They were created by the "ORCAD 10.0 Layout Plus" CAD software. LCSS adapter electronic schematics are present in the same folder. The project files of the schematics were created by "ORCAD 10.0 Capture". The file named "multisensore2_0.opj" is the main project file; by opening it by "ORCAD 10.0 Capture", it is possible to view and modify all the schematics files. Schematics and PCB files are also available as "pdf" documents in the "lcss adapter/pdf files/schematics" and "lcss adapter/pdf files/pcbs" subfolders respectively. LCSS adapter board is shown fully assembled in Figures 6 and 7. When the board is fully assembled, it is necessary to wire in short-circuit the two pins of the J11 and two pins of J13, as shown in figure 5. For the first use of the LCSS board, it is advisable to set the gain of the built-in amplifiers to the unit value. This operation can be carried out by using a little screwdriver and an ohm-meter. The resistive trimmers R14, R15, R23, R22, R30, R31, R38, R39, have to be set at their minimum possible value by rotating their little top screw (see figure 6).

Figure 5: The red arrows indicate the two pins of J11and J13 to short-circuit.


7

Figure 6: the black arrows and the black circle show the pins and the connector where the analog signals of the sensors have to be wired; while the red arrows and red circles indicate where the R14, R15, R23, R22, R30, R31, R38, R39 resistive trimmers are placed.


8

Figure 7: LCSS adapter bottom view.

The core of the LCSS adapter board is a PIC 18F4685 microcontroller by Microchip, which has to be programmed for the correct board operation. The tool needed to program the board is the "ICD2" programmer by Microchip. The necessary cable to connect the "ICD2" programmer to the LCSS board has to be assembled, as shown in figure 8. The cable is composed of an RJ11 female connector, a five positions male connector, and the wires. Optionally, the RJ11 connector can be fixed on a piece of a prototype board. The final appearance of the fully assembled cable is shown in figures 9 and 10. The electronic components needed for assembling both the LCSS adapter board and its programming cable are listed in the files placed in the subfolders "lcss adapter/bom/board" and "lcss adapter/bom/cable". In those files are also indicated the suppliers that sell all the required components. Once the programming cable and the LCSS board have been assembled, it is possible to burn the LCSS firmware on the board by using the "ICD2" programmer and the MPLAB IDE v. 8.66 distributed by Microchip (see https://www.microchip.com/development-tools/pic-and-dspic-downloads-archive (https://www.microchip.com/development-tools/pic-and-dspic-downloads-archive) ). The program to burn on the LCSS board microcontroller is the "lcss_adapter.hex", located in the subfolder "lcss_adapter/firmware". When the user is going to connect the programming cable to the J7 socket of the LCSS board, he has to be careful to insert the male connector correctly: pin n.1 of it has to be inserted in the pin n.1 of the J7 socket. All the files related to the LCSS firmware are available in the subfolder "lcss_adapter/firmware/project_files" for modifications. The code of the LCSS firmware is written in "C" language; PCH libraries distributed by CCS are required to modify and compile the source code (see: https://www.ccsinfo.com/product_info.php?products_id=PCH_full ).

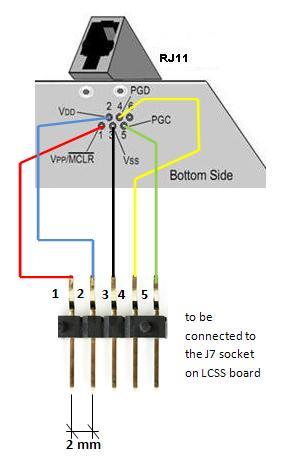
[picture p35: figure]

9

Figure 8: connections to make for assembling the cable to program the LCSS board.

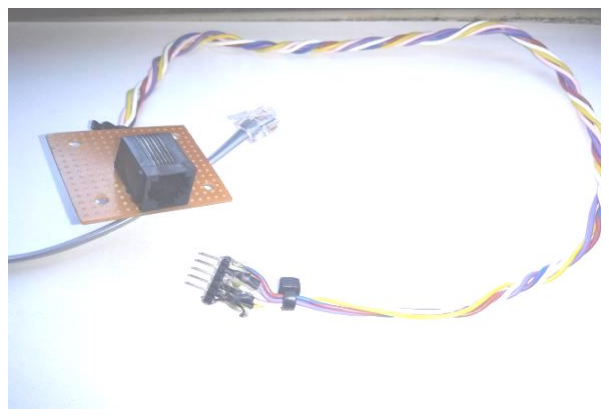
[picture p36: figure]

Figure 9: top view of the programmer cable for LCSS board.

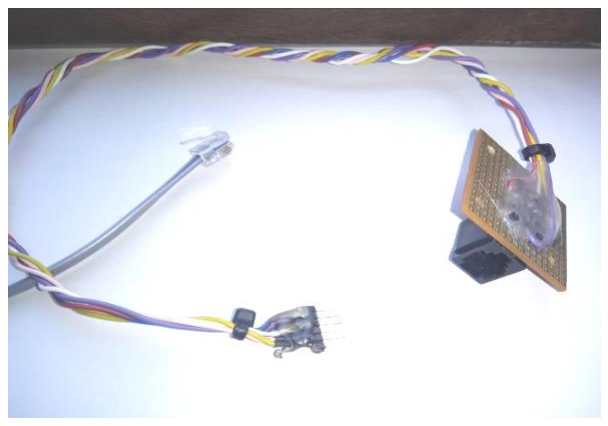
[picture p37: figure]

Figure 10: bottom view of the programmer cable for LCSS board.

Using the ADC Pi
The second option for using analog output interface devices with SentinAir is given by mounting the ADC Pi board on SentinAir. This board is provided by ABelectronics (https://www.abelectronics.co.uk/) (see figure 11, 12) and it is based on the MCP3424 microprocessor, which is an analog-to-digital converter. The software driver for MCP3424, and therefore for the ADC Pi board, is already available in the repository of
SentinAir in the folder “devices”. This board is featured by two MCP3424 microprocessors each
containing four analog inputs. Therefore, the total number of signals for each ADC Pi board is eight. The maximum analog-to-digital conversion accuracy provided by MCP3424 is 17 bits. The

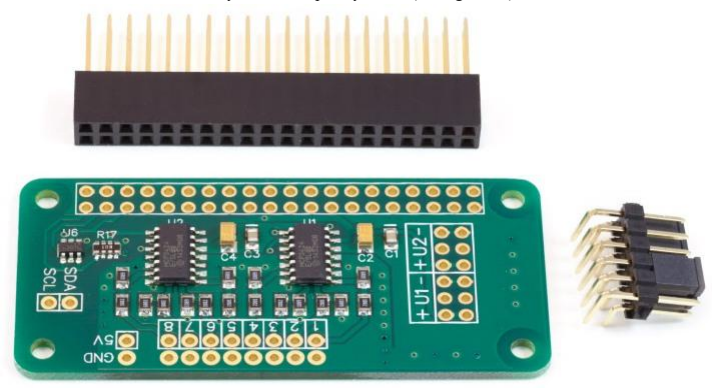
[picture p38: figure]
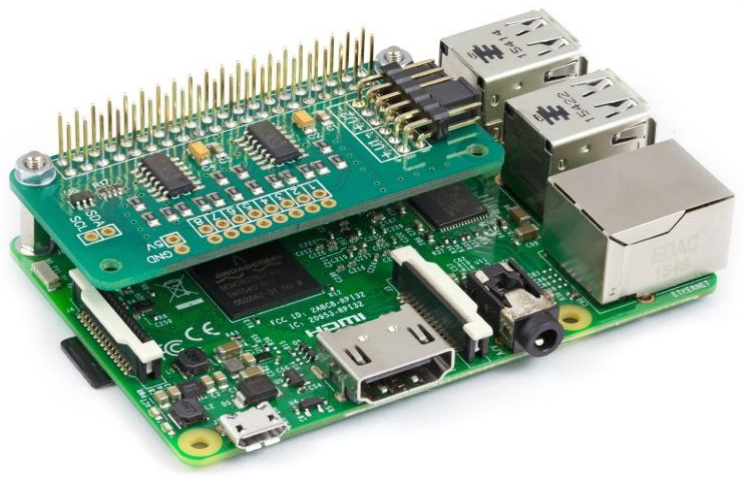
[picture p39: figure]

10

ADC Pi is attached to the Raspberry board through the Raspberry GPIO connector. This board is interfaced with the Raspberry through the I2C port. No electrical wiring is necessary to connect the ADC Pi board to Raspberry, because the power and the I2C bus connections are provided by the GPIO connector to insert directly on the Raspberry board (see figure 12).

Figure 11: ADC Pi board layout. The V1 and V2 terminals are devoted to the I2C address selection of the two MCP3424 microprocessors of the board. The jumpers of the connector on the right side of the picture set the I2c bus address of each microprocessor. The pins numbered from 1 to 10 are the analog inputs.

Figure 12: the ADC Pi connected to the Raspberry Pi through the GPIO connector.

11

SentinAir software installation (basic procedure) This is a quick procedure to install the SentinAir software making the minimum steps. If you desire
a higher level of customization, you can refer to the “SentinAir software installation”chapter of this
guide. The procedure is composed of two steps:
a) Installing the SentinAir sd card image
Download the latest SentinAir SD card image file. (https://drive.google.com/file/d/1Ex4GyDE1UydjNPgzCsWaSeaUH6ddkkUb/view?usp=sharing) Write it in an SD card having at least 2 GB (4 GB recommended) of memory space by using, for example, Win32diskimage.exe program (for Windows operative systems).
b) Enabling the use of the IMAP-SMTP module (optional)
To use the IMAP-SMTP module (see the chapters “SentinAir start up”, and “controlling SentinAir by e-mail”), please, follow the steps described in points 10 and 11 of the section “Installing the SentinAir software modules”.

SentinAir start-up after the basic installation procedure Supposing you have finished the a) point of the basic installation procedure, insert the SD card in the SentinAir device, plug one or more devices among the ones listed in table 1 into one of the system ports, and give power to SentinAir. After a few seconds, the green light starts blinking. Following this stage, the yellow light starts blinking. This means that the system is performing the port scanning. If one or more devices/sensors/instruments are found, the system automatically starts to acquire data (entering in the active monitoring mode and starting a new measurement session),
and the yellow light turns on. To stop the measurement session, you have to use the “SentinAir user
interface” and send the on-purpose command to the system (please, refer to the “Using the SentinAir user interface” chapter of this guide).

SentinAir software installation (advanced procedure)
The procedure described below allows skilled users to customize the SentinAir system during the installation process. All the software necessary to operate a SentinAir device runs on Raspbian Stretch Lite Operative System (OS); therefore, the first step is downloading and installing it on a SentinAir device or a Raspberry 3 B+ board. For a correct SentinAir software installation, please, follow in sequence the below procedures. For the first software installation, the user has to plug a keyboard into the USB port and a monitor into the HDMI port. Subsequently, it is possible to access the system via SSH connections by using programs such as putty.exe or WinSCP.exe (for Windows operative systems).
a) Installing Raspbian Stretch Lite operative system
1. Download the Raspbian Stretch Lite OS image into a computer from the link: https://www.raspberrypi.org/downloads/raspbian/ and flash it in an SD card memory featured by at least 2 GB of room by using, for example, Win32diskimage.exe program (for Windows operative systems).
2. Create a blank file called ssh (no extension). Save this file in the root of the MicroSD card with the flashed image. This operation is for enabling SSH connections at start-up.

12

3. In order to allow SentinAir to connect to a Wi-Fi network when it turns on, create a wpa_supplicant.conf file and write inside the following lines:

ctrl_interface=DIR=/var/run/wpa_supplicant GROUP =netdev
update_config=1
country=<your country code>
# home network; allow all valid ciphers

network={
ssid="<your network name>" scan_ssid=1
key_mgmt=WPA-PSK
psk="<your network password>"
}

Save and close the file. If you are using the Windows operative system to write the file, you have to convert it to the Linux/Unix standard. To do this, it is possible to use the program dos2unix.exe. Save wpa_supplicant.conf in the root of the MicroSD card with the flashed image.
4. Plug the Sd card in the Raspberry board and power it.
5. Find the SentinAir IP address by using programs to scan the network set in the wpa_supplicant.conf; for example, for this purpose, there is an "app" for the Android system called FindPi. Once found which is the SentinAir device IP address, it will be possible to continue the installation process by connecting to SentinAir from another computer via SSH connections. To do this, for example, it is useful the program putty.exe, if the computer has a Windows operative system running on it.
b) Preparing Raspbian for SentinAir installation
1. Power the SentinAir device or the Raspberry 3 B+ board, log in it, and type the command: sudo raspi-config.
2. To set the device name, select Network Options/Hostname and insert the device name. It is mandatory to enter a name with a "hyphen" inside, for example, sentinair-S1. This is for the correct functioning of SentinAir software. The part of the name following the hyphen is the identity number you choose for the device. Do not exit from raspi-config yet.
3. To use the serial port for connecting devices, select Interfacing options/Serial and then press in sequence "NO" and "YES". If everything is fine, you should see the message "The serial login shell is disabled. The serial interface is enabled". Then press "OK".
4. To use I2C ports for connecting devices, select Interfacing options and then P5 I2. Select “yes” to enable the I2C ports.
5. To expand the use of the memory on your SD card, select Advanced Options/ expand Filesystem. Select then FINISH and reboot the system.
6. Run the command sudo nano /etc/hosts and update the file by modifying the line: "127.0.0.1 raspberrypi" in the line: "127.0.0.1 <device-name>", where <device-name> has to be the same name selected in the step 2 (which is, as for example sentinair-S1). Reboot the system.

13

7. To complete the configuration for the serial port called /dev/ttyAMA0, we have to disable the Bluetooth service that uses this port and set it as a general-purpose serial port. To do this, type sudo nano /boot/config.txt, and then add at the end of the file, the row: dtoverlay=pi3-disable-bt. Save and close the file. After doing this, prevent Bluetooth service to use serial port by typing the command: sudo systemctl disable hciuart. Then reboot the system by running sudo reboot.
8. Update the Raspbian repository by typing the command: sudo apt-get update.
9. From now on, to perform the next steps of installation, it is needed to log into the system with the help of a keyboard and a monitor. This is necessary because the built-in Wi-Fi modem will turn in a Wi-Fi access point, and therefore it is impossible to continue while SentinAir is connected to a pre-existing Wi-Fi LAN. Moreover, to connect the device to the Internet, it is going to be necessary a USB stick modem with a valid SIM card enabled by an Internet Service Provider to connect to the Internet (for example, the model Huawey E303 does not require installation procedures). This is why the Ethernet port will be reserved to connect instruments to form a local "stand-alone" LAN. Therefore run sudo halt to stop the system, plug the USB stick modem, the keyboard, and a monitor, then log in again.
10. Download and install dnsmasq and hostapd by typing the command sudo apt-get install -y dnsmasq hostapd.
11. Stop the execution of the software just installed by running the commands: sudo systemctl stop dnsmasq and sudo systemctl stop hostapd
12. Set a static IP for the system and configure dhcpcd by opening the file dhcpcd.conf with the command sudo nano /etc/dhcpcd.conf and add at the end of the file the lines:
interface wlan0
static ip_address=192.168.4.1/24 (or an alternative IP address you choose)
nohook wpa_supplicant
dhcp-range=192.168.4.2,192.168.4.100,255.255.255.0,24h
interface eth0
static ip_address=192.168.20.1/24
static routers=192.168.20.1
nogateway
Save and close the file.
13. Configure the hostapd software by creating the file hostapd.conf , to do this, run the command sudo nano /etc/hostapd/hostapd.conf . Then insert in the file the following lines:
interface=wlan0
driver=nl80211
ssid=device-name (for example: sentinair-S1)
hw_mode=g
channel=7
wmm_enabled=0
macaddr_acl=0
auth_algs=1
ignore_broadcast_ssid=0
wpa=2

14

wpa_passphrase=sentinair1
wpa_key_mgmt=WPA-PSK
wpa_pairwise=TKIP
rsn_pairwise=CCMP
Then save and close the file.
14. Complete hostapd configuration by typing sudo nano /etc/default/hostapd. Then modify the line:
#DAEMON_CONF=””

in the new line
DAEMON_CONF=”/etc/hostapd/hostapd.conf “
Save and close the file.
15. Run the command sudo nano /etc/init.d/hoastapd and replace the line
DAEMON_CONF=
whit the line
DAEMON_CONF=/etc/hostapd/hostapd.conf.
Save and close the file.
16. Run the command sudo nano /etc/dnsmasq.conf and add at the end of the file the following lines:
interface=wlan0
dhcp-range=192.168.4.2,192.168.4.100,255.255.255.0,24h.
Save and close the file.
17. Finally, run the commands:
sudo systemctl restart dhcpcd.
sudo systemctl unmask hostapd sudo systemctl enable hostapd sudo systemctl start hostapd
sudo service dnsmasq start
sudo reboot
c) Installing Lighttpd webserver
1. Install lighttpd by the command
sudo apt-get install –y lighttpd.
2. Enable the cgi-bin module of the web server by the command sudo lighty-enable-mod cgi
3. Open /etc/lighttpd/conf-available/10-cgi.conf and modify the lines:
$HTTP["url"] =~ "^/cgi-bin/" {
cgi.assign = ( "" => "" )
}
in
$HTTP["url"] =~ "^/cgi-bin/" {
alias.url += ("/cgi-bin/"=>"/var/www/cgi-bin/") cgi.assign = ( "" => "" )
}
4. Run the command sudo service lighttpd force-reload

15

5. Create the folders: /var/www/html/data, /var/www/html/log and /var/www/html/img. Give them the read, write, and execute rights for all the users.
6. Rename the file /var/www/html/index.lighttpd.html in /var/www/html/index.lighttpd.html_. Copy the files index.html, sentinair.jpg, and btnplt.png in the folder /var/www/html/.
7. Copy the files fileinspector.py and surianocliweb.py in the folder /var/www/cgi-bin/ and give them read, write, and execution rights for all the users. Then reboot the system.
d) Installing the SentinAir software modules
1. Install python3-serial by running the command sudo apt-get install python3-serial.
2. Install pip3 by running the command sudo apt-get install python3-pip
3. Install the library RPi.GPIO by running the command sudo apt-get install python3-RPi.GPIO.
4. Install the library libscrc by running the command sudo pip3 install libscrc.
5. Install the library smbus2 (for i2c manging) by typing the command sudo pip3 install smbus2
6. Install the library python3-matplotlib by running the command sudo apt-get install –y python3-matplotlib
7. Reboot the system.
8. Create the folder /home/pi/sentinair. SentinAir software files have to be mandatorily copied into this folder
9. Copy in /home/pi/sentinair/ the following files and folders:
- sentinair.py
- sentinair_system_manager.py
- sentinair_system_installer.py
- imap-smtp-interface.py
- imap-smtp-monitor.sh
- mail-config.sentinair
- devices
The folder "devices" is the folder where devices drivers have mandatorily to be placed.
10. In order to get started SentinAir software when the system boots, insert the following lines in the file /etc/rc.local before the line “exit 0”:
python3 /home/pi/sentinair/sentinair_system_manager.py&
WARNING: if you are editing rc.local on a Windows OS, remember to convert it in Unix/Linux format through the “dos2unix.exe” utility.
11. Open the “mail-config.sentinair” file and put your e-mail account data in the lines without
the comment character (#) avoiding inserting the “space” character, like the example below: MAIL_ADDRESS="my-email_address@my_company.com" MAIL_PWD="my-email-account-password"
SMTP_SERVER="my-smtp-server-url"
IMAP_SERVER="my-imap-server-url"
12. Reboot the system

16

Setting up SentinAir internet connection
The USB stick modem Internet plugged into one of the USB ports available gives the channel to reach a SentinAir system from the. If a Huawey E303 is used for the purpose, no installation procedures are required. Other USB stick modem models have not been tested yet. Internet Service Providers (ISP) usually do not give public IP addresses to the user; therefore, SentinAir could not be reachable from anywhere. To overcome this issue, it is possible to use the "IP tunneling" services that give the possibility to get around this hurdle. Prices of these services can vary from free to a few Euros per month. Examples of web companies offering these services are www.dataplicity.com, or www.pitunnel.com or. https:\\remote.it.

SentinAir start-up
SentinAir gets started when the electronic hardware is powered, alternatively, by typing the command: sudo python3 /home/pi/sentinair/sentinair_system_manager.py. After few seconds the system is powered, you should see the green light asynchronous blinking, which indicates that the CPU is exchanging data with the SD memory and the system is setting up (see table 3).

Table 3: check light behaviors and their meaning
LED | LED STATUS | MEANING
RED | OFF | System turned off
| BLINKING | Sensor fault (the user must see the log file to get more information)
GREEN | ASYNCHRONOUS BLINKING | Data exchange activity between CPU and SD memory
YELLOW | OFF | System active, monitoring not active
| FAST BLINKING | The system is performing the port scanning to find which devices are connected
| SLOW BLINKING | The shut-down procedure is going on, following the shut-down button pressing
| ON | Monitoring active

When SentinAir gets started, before getting ready, it performs some preliminary operations to work appropriately. Firstly, it makes blink the yellow check light to indicate that the system is performing the scanning of the system ports to find which devices, among the ones whose driver is already installed in the system, are plugged into. When a device is found, it got connected to the system. This operation might last a few seconds, and during this time, you should see if you have a monitor plugged into the HDMI port, system messages on the screen. From now on, all the relevant operations and events are logged in the on-purpose log file of the system manager (the default name is sentinair-log.txt). During this period, the system cannot accept commands from the user; sometimes, it can last a few minutes. As soon as this operation is completed, SentinAir reads the file status.sentinair, where there is information about the device status: "standby", or "active monitoring". If the system is in "active monitoring" status, a new measurement session gets started; therefore, the yellow led check light turns on, and a new file containing the measurement data is created. The last operation of the start-up phase is the sending of an e-mail to the e-mail address indicated in the file mail-config.sentinair if the USB stick modem is plugged into the system (see figure 14). In the current version of the software, SentinAir configuration is featured by a static IP on the cable Ethernet port. Devices connected to this interface will form a "stand-alone" net that is

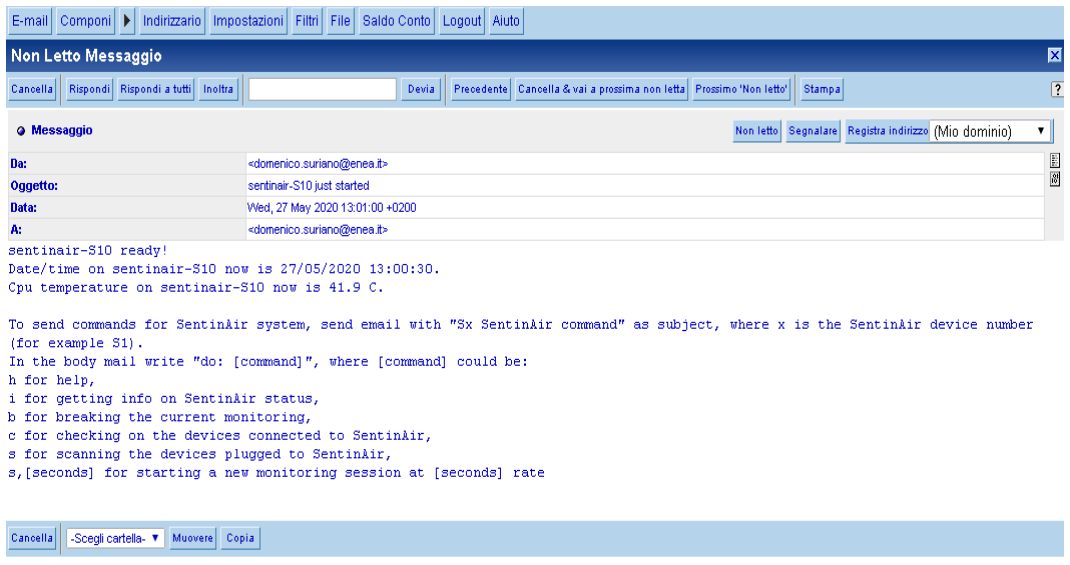
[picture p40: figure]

17

not connected to the Internet. If the user needs to connect more devices, for example, it is possible to use an Ethernet switch.

Figure 14: E-mail sent by SentinAir at start-up time.

Installing devices drivers in SentinAir
SentinAir can read data from any device as long as the specific driver of the device is installed in the system. It is mandatory that the device driver files have to be in the folder /home/pi/sentinair/device. In order to easily install drivers, the user can log into the system by SSH connection via the Wi-Fi link through the LAN set up by SentinAir. Then the user has to use the module sentinair_system_installer.py by opening it through the command:
sudo python3 /home/pi/sentinair/sentinair_system_installer.py.
Once opened the installer, the commands available are listed in table 4.

Table 4: commands available for the SentinAir system installer
Command function | Command syntax | Example | Effect
Device driver installation | i,device_name.py | i,pms3003.py | Installs the driver for the device pms3003
Device driver uninstalling | u,device_name.py | u,pms3003.py | Uninstalls the driver for the device pms3003
Checking the current drivers installed | c | c | Displays a list of the drivers currently installed
Modifying the current path of the system manager module | m | m | Writes in the file "manager_dir.sentinair" the new path of the manager system module


18

Asking for the commands list available | h | h | Displays a brief manual where are shown the commands
Quit the program | q | q | Quits the programs

An example of sentinair_system_installer.py use is shown in figure 15. After updating the system with new installations, it has to be rebooted or restarted.

Figure 15: the installer user interface

19

Using the SentinAir user interface
SentinAir system main interface is provided by the sentinair.py module. The user has to log into the system by SSH connection via the Wi-Fi link through the LAN set up by SentinAir. To open the SentinAir user interface, type the command:
python3 /home/pi/sentinair/sentinair.py.
Once opened the user interface, the commands available are listed in table 5.

Table 5: commands available for the SentinAir user interface
Command function | Command syntax | Example | Effect
Starting a new monitoring session | s,seconds | s,60 | A new monitoring session gets started. Every 60 seconds, device measurements data are read and stored in a file
Stopping a measurement session | b | b | Stops the current measurement session
Retrieving information about the system status | i | i | Displays information such as the devices currently connected to the system, the sampling rate of the measurement session, or if the system is on standby.
Retrieving information about the devices connected to the system | c | c | The system returns the information about the connected devices: identity, units of measurements, current measurements
Asking for the commands list available | h | h | Displays a brief manual where are shown the commands
Scanning the ports and connecting the devices plugged into SentinAir ports | s | s | The system scans all the ports (USB, Ethernet, etc.) and recognizes if one of the installed devices is plugged into
Quit the program | q | q | Quits the programs

An example of the use of the SentinAir user interface is shown in figure 16. If the system is not in active monitoring mode (you can see this by checking the yellow light, which should be off), the
message “No measurement session ongoing” is shown. If you want to start acquiring data from sensors (putting the system in active monitoring mode), you have to type the command “s,60”. This
way a monitoring session will start at 60 second sampling rate and the yellow check light will turn on.


20

Figure 16: the SentinAir user interface.

Setting SentinAir system date and time
SentinAir system has not a hardware Real Time Clock (RTC). If the device is connected to internet, it automatically updates date and time of the system, otherwise, if necessary, the user must update manually it. To carry out this operation, no measurement session must be active; in this case, before setting correct date and time, the user must stop the current measurement session by opening the
SentinAir user interface and by typing the command “b” (see table 5). Once done this operation, the user must quit the program by launcing the “q” command (see table 5), and subsequently, he can set the current date and time by running the Linux command “date” as follows: “sudo date –s=”YYYY-
mm-dd hh:mm:ss”. For example, if you want to set the date and time on the 23th of February 2022 at 23:44:21, you must type the command: “sudo date –s=”2022-02-23 23:44:21”.

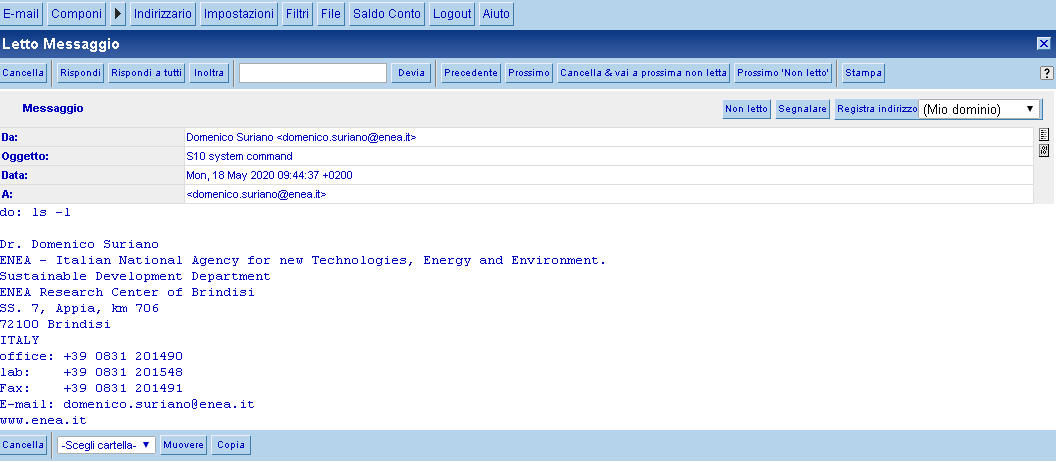
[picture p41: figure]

21

Controlling SentinAir by e-mail
SentinAir has been designed for being used in all that cases where it is necessary to perform experiments or measurements in remote areas, where possibly the internet link is weak or unstable, and therefore, where it is difficult the remote control and the data download from the device. For this purpose, commands and data can be exchanged by e-mail sending and receiving. SentinAir checks periodically on the IMAP server configured in the imap-smtp-interface.py for the presence of e-mails containing commands, and when the radio signal allows it, sends back the response. The imap-smtp-interface.py module is optional, and it is not essential for SentinAir operation. If it is present, it is launched by sentinair_system_manager.py at start-up. The user can send commands through e-mail for both the SentinAir system or for the operative system programs and services. A typical SentinAir command is, for example, "s,60", which causes the start of a new measurement session at 60 seconds sampling rate. A command directed for the operative system could be, for example, "ls –l", which returns the list of files and directories contained in the current system directory. E-mails containing commands for the operative system must have as subject the text: "device_ID system command",
where the "device_ID" is the part of the device name which follows the hyphen. For example: if the device name was set as "sentinair-S1" during the software installation process, then the device_ID will be "S1" (see figure 17 and 18). Moreover, e-mails containing commands directed to SentinAir software must have as subject the text:
"device_ID SentinAir command" (please, mind the correct case of letters).
The body of the e-mail must have a line where there is "do: command". For example: "do: s,60" (please, mind the "space" character between "do:" and the command). It is possible to download every kind of file present in the device by sending an e-mail having the subject as: "device_ID system command", and the body having the line as: "do: fget /path_of_the_file/file_to_download" (mind the space characters between "do:" and "fget" and between "fget" and "/path_of_the_file/file_to_download"). For example: "do: fget /var/www/html/log/sentinair-log.txt".

Figure 17: e-mail sent to SentinAir containing a command for the operative system

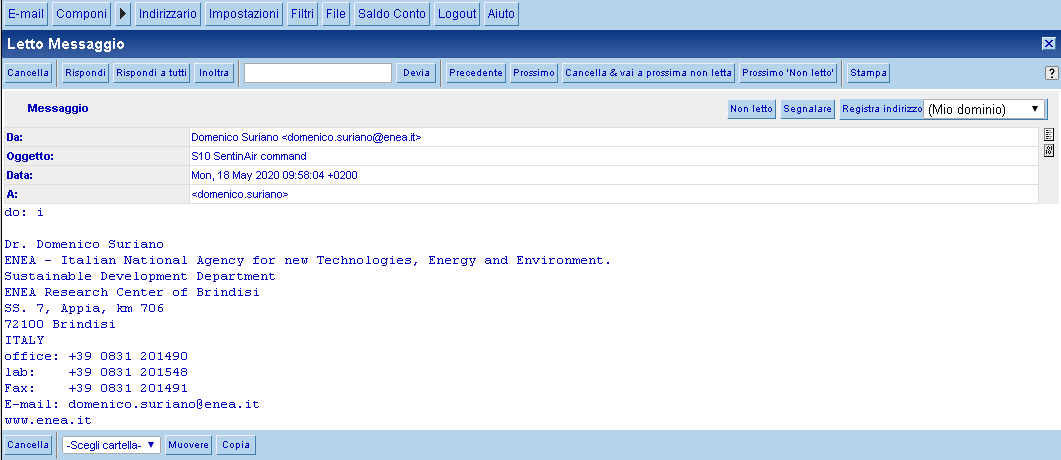
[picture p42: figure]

22

Figure 18: -mail sent to SentinAir containing a command for SentinAir system

SentinAir operations featuring the measurement session When a new measurement session gets started (for example, by the command "s,60"), the yellow led check light turns on. Three new files are created: the file containing the records of the measurements along with the timestamps (see figure 19) and named: "device_name_date_time.txt" (for example sentinair-S1_2020-02-03_09-30-15.txt), the file containing hourly averages of measurement and named: "device_name_date_time_hourlymeans.txt" (for example: "sentinair-S1_2020-02-03_09-30-15_hourlymeans.txt"), and the file containing the daily averages of the measurements, named: "device_name_date_time_dailymeans.txt" (for example: "sentinair-S1_2020-02-03_09-30-15_dailymeans.txt"). Hourly and daily averages are computed in real-time by the module sentinair_system_manager.py, and they are stored in the path indicated in that module (which is for default: "/var/www/html/data"). Another operation performed by the sentinair_system_manager.py module during the measurement session is the plotting of each magnitude measured by each of the devices connected to SentinAir. The plots are stored in jpg files placed in the path "/var/www/html/img" (which is their default path). Those files are encapsulated in web pages and served to the user when he connects by a web browser to SentinAir.

Figure 19: a file containing records of a SentinAir measurement session.

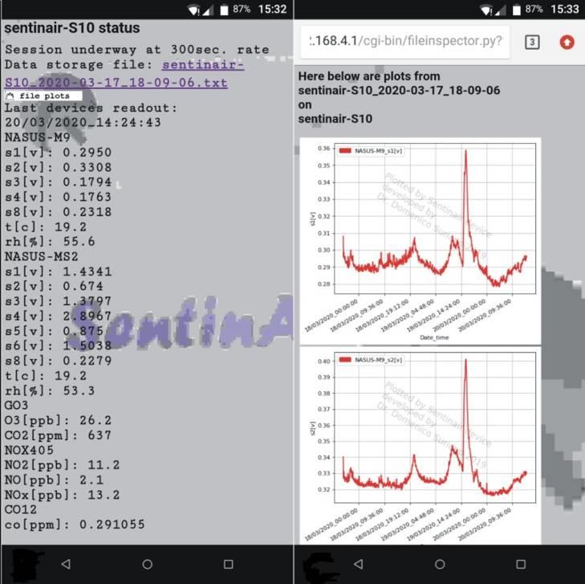
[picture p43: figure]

23

SentinAir web pages
The user can monitor SentinAir activity by connecting through a web browser to SentinAir (see figure 20). As for the other user interfaces given by the sentinair.py module and the sentinair_system_installer.py module, the webserver of SentinAir can be reached by connecting through a Wi-Fi link at the address set in the /etc/dhcpcd.conf file (which default is 192.168.4.1), or through internet connections via the selected "IP tunneling" service. Web pages of SentinAir allow the user to download all data and log files that are in the system.

Figure 20: web pages from SentinAir

Shutting down SentinAir
To shut down the system through the button shown in figure 4, the user has to press it and hold it pressed until the yellow light starts blinking. At that moment, it is possible to release the button. Before taking off the power from the system, you have to wait that the yellow light stops blinking and after that, wait the green light stops blinking and the red light turns off. Optionally, you have to
type the “sudo halt” command to the operative system running on the Raspberry board to properly
shut-down the system.

How to write device drivers for SentinAir
The creation of new device drivers for SentinAir is highly expected. It is desirable that researchers, or users, write drivers for their own devices to use with the SentinAir system. In order to facilitate
this task, driver templates have been written and stored in the folder “devices/device-driver-
templates” of the SentinAir Github repository. (https://github.com/domenico-suriano/SentinAir) When a new driver is going to be written, the user must follow some rules in order to get it fully compatible and operating with the pre-existing software. Some of these rules are common to all types of devices (USB, serial, I2C, Ethernet), while there are rules specific for each type of sensor/device. We recall that sensors or devices featured by

24

analog output interfaces must be used with the LCSS adapter board (having a USB output interface), or with the ADC Pi (having an I2C output interface). A good way to getting started with
writing new device drivers is by modifying the template file related to your device type (“ethernet-
device-template.py”, “usb-device-template.py”, “serial-device-template.py”, or “i2c-device-template.py”).
Here below it is shown a step by step procedure which hopefully will help the user to correctly write new device drivers. In doing this, we will report some examples referring to the files of some
drivers already developed (“nox405.py”, ” ac32.py”, ”bh1750.py”), and to the files of the driver
templates.
1. Import the necessary library. For I2C devices, “smsbus2” is mandatory (see “bh1750.py” and “i2c-device-template.py”), for USB and serial devices “serial” is mandatory (see “nox405.py” and “serial-device-template.py”), for Ethernet devices “socket” is mandatory (see ” ac32.py” and “ethernet-device-template.py”). Also import other libraries specific for your device operation (see for example “time” and “_thread” in “nox405.py”)
2. Set the mandatory constant strings CONNECTION_TYPE, DEVICE_IDENTITY, and DEVICE_SENSORS common for all the device types following the indications in the driver template files (“ethernet-device-template.py”, “usb-device-template.py”, “serial-device-template.py”, or “i2c-device-template.py”). The DEVICE_SENSORS string contains the magnitude names measured by the device, separated by a semicolon character; for example (see “nox405.py”): "no2[ppb];no[ppb];nox[ppb]". Then set the constants specific for each type of device: I2C_ADDRESSES, which must be a Python list of integer values (for I2C devices, see “bh1750.py” and “i2c-device-template.py”), ETH_ADDRESSES, which must be
a list of strings (for Ethernet devices, see ” ac32.py” and “ethernet-device-template.py”),
DEVICE_BAUD_RATE, which must be an integer value (for serial and usb devices, see
“nox405.py” and “serial-device-template.py”). Set the other constants (if any) specific for
your device operation.
3. Create the device class name. It is mandatory that the class name must be the same as the driver file name with the first letter capitalized. For example: the driver “nox405.py” contains the class Nox405.
4. In the “__init(self)” method of the device class, you can find the mandatory variables
common for all the device types:
self.identity = DEVICE_IDENTITY
self.connection_type = CONNECTION_TYPE
self.sensors = DEVICE_SENSORS.
There are also variables specific for a device type. For I2C device (see “bh1750.py” and “i2c-device-template.py”), you will find:
self.addresses = I2C_ADDRESSES
self.device_address = 0x00.
For Ethernet devices you will find (see ” ac32.py” and “ethernet-device-template.py”): self.addresses = ETH_ADDRESSES
self.device_address = None
self.sk = None
For serial or usb devices you will find (see “nox405.py” and “serial-device-template.py”):

25

self.baud_rate = DEVICE_BAUD_RATE
self.portname = ""
self.port = None.
The user must not modify the above-mentioned lines, but he can add variables necessary and
specific for his device operation (see, for example, the “__init(self)” method in the file “nox405.py”).
5. The device class must contain the following methods common for all the device types; they are:
def getConnectionType(self):
return self.connection_type def getIdentity(self):
return self.identity
def getSensors(self):
return self.sensors
def setIdentity(self,idstring):
self.identity = idstring
Moreover, for a specific device type, there are other mandatory methods. For I2C devices
device (see “bh1750.py” and “i2c-device-template.py”), we have:
def getConnectionParams(self):
return self.addresses
def terminate(self):
self.device_address = 0x00.
For Ethernet devices (see ” ac32.py” and “ethernet-device-template.py”), we have:
def getConnectionParams(self):
return self.addresses
def terminate(self):
try:
self.sk.close()
except:
return
def __del__(self):
try:
self.sk.close()
except:
return
For usb or serial devices (see “nox405.py” and “serial-device-template.py”), we have:
def getConnectionParams(self):
return [self.portname,self.baud_rate]
def terminate(self):
try:
self.port.close()
except:
return

26

def __del__(self):
try:
self.port.close()
except:
return.
The user must not modify the above-listed methods, but he can add other ones specific for
his device operation (see, for example, the “nox405.py”, ” ac32.py”, “bh1750.py”).
6. The class must have the method called “connect(self,address)” in case of I2C or Ethernet devices, or “connect(self,portname)” in case of serial or usb devices. This method detects if the device is connected and finds the connection parameters, for example, if it is searching for an Ethernet or I2C device, it finds the device address; or, if it is searching for a USB or serial device, it finds the USB port. If no device is found, it returns the "0" value, otherwise, it returns "1". For implementing the "connect" method, I suggest to request data from the device and see if it responds. If this operation succeeds, it means that the device is correctly
connected, and in this case, the 1 value will be returned (see, for example, the “nox405.py”, ” ac32.py”, “bh1750.py”).
7. The device class must have the method "sample(self)" that must return a string containing the last measurements separated by a semicolon mark. An example of a string returned by this method could be: “27,76;0,1234;456,9”. It is mandatory that the fields contained in the string must be in the same number as the ones set in the DEVICE_SENSORS string. For example: if DEVICE_SENSORS=“no2[ppb];no[ppb];nox[ppb]” (see “nox405.py”), then the "sample(self)" method must return “27,76;0,1234;456,9".

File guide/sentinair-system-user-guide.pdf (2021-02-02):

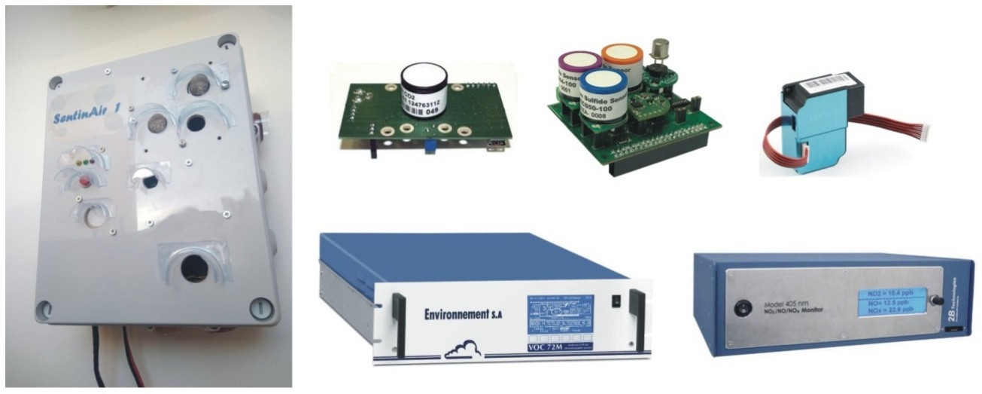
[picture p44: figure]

1

## User Guide

### Project designer and developer

Dr. Domenico Suriano, (https://materiali.sostenibilita.enea.it/people/domenico-suriano) domenico.suriano@enea.it

This user guide version (v. 1.3) refers to the SentinAir system version 1.3 available at the Github SentinAir repository. (https://github.com/domenico-suriano/SentinAir)

### Description

SentinAir is a device designed and developed for data acquisition from diverse types of instruments, sensors, or devices (see figure 1). The core of the system is the Raspberry 3 B+ board; therefore, the software presented in this guide can be installed either on a SentinAir device or a Raspberry 3 B+ board. Devices have to be plugged into SentinAir by USB, Ethernet, serial UART, SPI, or I2C port. Currently, the system has been tested only with devices connected by the USB, I2C, Ethernet, and serial UART port available on the Raspberry board, which is the "brain" of SentinAir. The system is based on command line interfaces, except for the web pages served by the webserver installed inside.

Figure 1: on the left, SentinAir device. On the right, some devices currently tested by SentinAir.

2

The system automatically recognizes the devices or instruments plugged into SentinAir through their specific driver, written in Python. The drivers currently developed are listed in table 1.

Table 1: device drivers developed currently for SentinAir and available in the github repository.
Sensor or device | | | Device driver | | Connection interface | Supplier or manufacturer
BME280 (atmospheric pressure, temperature, and relative humidity) | | | | bme280.py | I2C | Bosch Sensortec
BH1750 (luxmeter) | | bh1750.py | I2C | ROHM semiconductor
MCP342x on ADC Pi board (to use devices having analog output signals) | | mcp342x.py | I2C | Microchip
IRC-A1 (CO2 sensor) | | | irca1.py | USB | Alphasense
PMS3003 (PM sensor) | | | pms3003.py | TTL serial port | | | Plantower
Multisensor board (to use devices having analog output signals) | | | | multisensor_board.py | USB | Tecnosens
106L GO3 PRO package (CO2 and O3 monitor) | go3.py | USB | 2B technologies
405nm (NOx monitor) | | | nox405.py | USB | 2B technologies
LCSS USB adapter (to use devices having analog output signals) | | | | lcss_adapter.py | USB | Designed and built in our lab
CO12M (CO chemical analyzer) | | | | co12m.py | Ethernet port | | Environnement
AF22M (SO2 chemical analyzer) | | | | af22.py | Ethernet port | | Environnement
AC32M (NOx | | chemical analyzer) | | ac32.py | Ethernet port | | Environnement
O342M (O3 chemical analyzer) | | | | o342.py | Ethernet port | | Environnement
VOC72M (VOC chemical analyzer) | | | | v72m.py | Ethernet port | | Environnement

## SentinAir hardware

SentinAir is a modular and flexible system. The system hardware can be assembled in a minimal (see figure 2), or a typical configuration (see figure 3). The minimal hardware is composed of:

- a Raspberry 3 B+ board
- a class 10 SD card featured by a memory capacity of at least 2 GB (4 GB recommended),.
- a 5V power source capable of providing a direct current of 3A maximum. At the moment, the system has been tested with a switching ac/dc adapter (see figure 2).

The minimal configuration allows the user to use sensors/devices/instruments featured by a USB, serial UART, I2C, or Ethernet output interface, while analog output interfaces devices must be used with one of the analog-to-digital converter boards featuring the SentinAir typical hardware configuration. Ethernet or USB devices must be connected through the Ethernet and USB sockets (see figure 2), while I2C and serial devices must be connected to the Raspberry GPIO connector following the indications of figure 3.

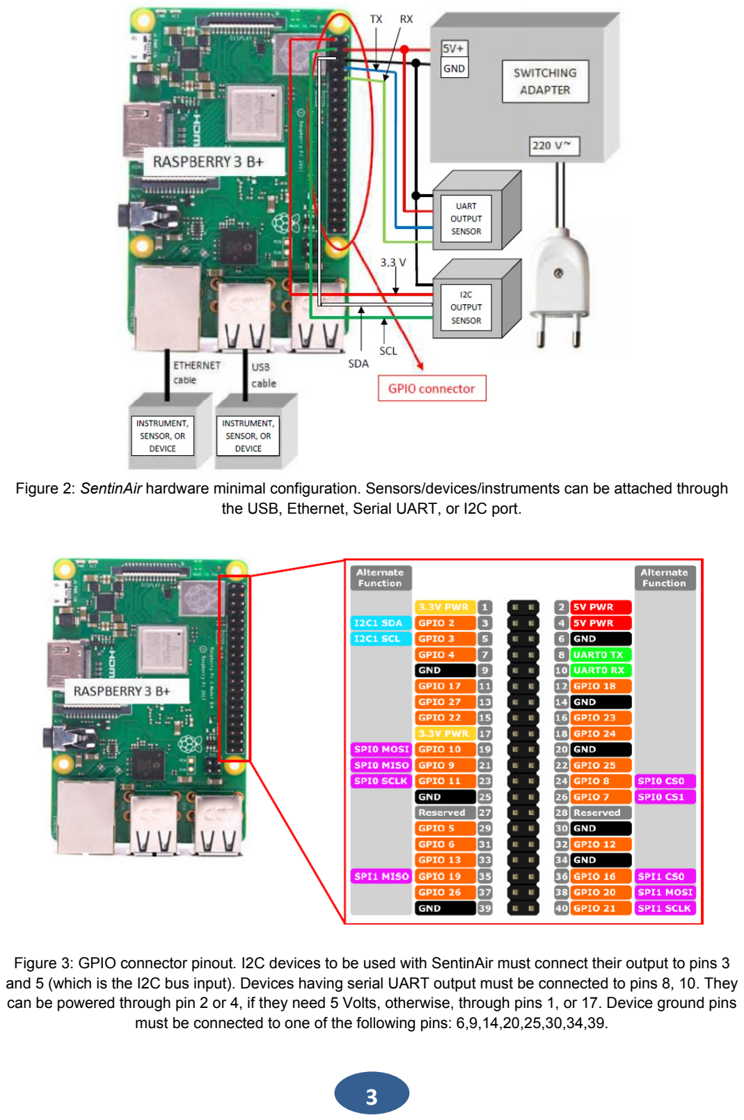
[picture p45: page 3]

3

Figure 2: SentinAir hardware minimal configuration. Sensors/devices/instruments can be attached through the USB, Ethernet, Serial UART, or I2C port.

Figure 3: GPIO connector pinout. I2C devices to be used with SentinAir must connect their output to pins 3 and 5 (which is the I2C bus input). Devices having serial UART output must be connected to pins 8, 10. They can be powered through pin 2 or 4, if they need 5 Volts, otherwise, through pins 1, or 17. Device ground pins must be connected to one of the following pins: 6,9,14,20,25,30,34,39.

4

The typical hardware configuration of a SentinAir system is shown in figure 4, and it is composed of:
- A Raspberry 3 B+ board,
- a class 10 SD card featured with a memory capacity of at least 2 GB (4GB recommended),
- The check light system made of three LEDs and three 120 Ohm resistors. They are going to indicate the three possible states of the device: standby (yellow LED off), active monitoring (yellow LED on), and fault (red LED blinking),
- A push-button to properly shut down the whole system,
- A USB stick modem (the system has been tested with a Huawei E303),
- The expansion board, which is necessary to enable the simultaneous multiple connections of sensors. This board is provided by header pin connectors through which devices can be wired for the power supply or I2C bus interfacing. Three header pin connector rows provide 5, 3,3 Volts power supply, and ground connections; in addition to them, the other two pin rows offer a quick way to connect the devices SCL and the SDA signal to the mainboard I2C bus (see figure 4).
- An analog-to-digital converter board capable of giving output data on the USB, I2C, or Ethernet port. This board is necessary to convert analog outputs of sensors into digital data. In fact, the Raspberry board, on which the SentinAir system is based, has not got a built-in analog-to-digital converter; therefore, without it, the use of sensors/devices having analog output interfaces could not be possible. The user can use for this purpose any board that requires a power of 5 V and 0,2 A maximum. For example, the ADC Pi board based on the MCP3424 microprocessor by Microchip and supplied by ABelectronics (https://www.abelectronics.co.uk/) can fit the purpose. Another option is given by the LCSS adapter board (LCSS stands for Low-Cost Small commercial gas Sensors), which has been designed and developed to make the analog-to-digital conversion in an optimum way. The LCSS adapter board has been designed to minimize as much as possible the effects of the additional unwanted electronic noise, which may affect the conversion. Moreover, it has a 16-bit analog-to-digital converter that ensures a high resolution.

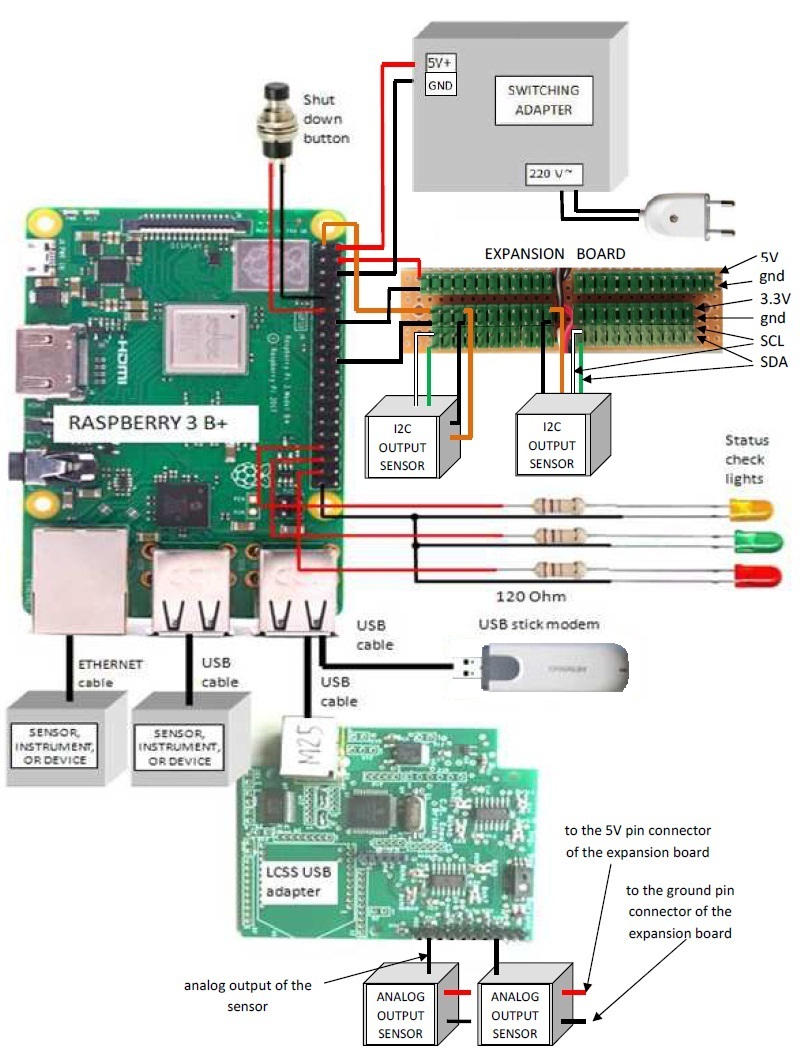
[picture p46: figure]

5

Figure 4: SentinAir hardware typical configuration. It includes an analog-to-digital converter board which enables the use of devices/sensors having analog output interfaces. This board can be the LCSS adapter or the ADC Pi by ABelectronics.

## LCSS adapter assembly and setup

The LCSS adapter board allows the use of devices having analog output interfaces, and it is powered through its USB port. It converts the input analog signals into digital data that are given as output through the USB port. The analog outputs of the devices to be used with the LCSS adapter have to be wired to the J22 connector of the LCSS board (pins 4 to 11, see figure 6). These signals must be in the range 0 - 3,3 Volts. The LCSS adapter has a built-in temperature and relative humidity sensor. Eight analog-to-digital (ADC) converters feature it. They are high resolution (16

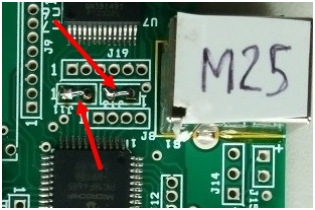
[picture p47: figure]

6

bits) converters, each of them having a signal amplifier and electronic noise filter. The user can set the gain of each amplifier through the resistive trimmers R14, R15, R23, R22, R30, R31, R38, R39 placed on the LCSS board (see figure 6). LCSS board can be used with the RN42XV Bluetooth adapter, even though its use is not necessary for the SentinAir system. The LCSS board is also designed to be used with rechargeable Li-Ion batteries. They have to be wired to the J15 connector (see figure 5), and they are automatically charged through the USB port. The use of batteries is not necessary for the SentinAir system.
Printed Circuit Board (PCB) files for LCSS assembly and setup can be found in the folder "lcss adapter". They were created by the "ORCAD 10.0 Layout Plus" CAD software. LCSS adapter electronic schematics are present in the same folder. The project files of the schematics were created by "ORCAD 10.0 Capture". The file named "multisensore2_0.opj" is the main project file; by opening it by "ORCAD 10.0 Capture", it is possible to view and modify all the schematics files. Schematics and PCB files are also available as "pdf" documents in the "lcss adapter/pdf files/schematics" and "lcss adapter/pdf files/pcbs" subfolders respectively. LCSS adapter board is shown fully assembled in Figures 6 and 7. When the board is fully assembled, it is necessary to wire in short-circuit the two pins of the J11 and two pins of J13, as shown in figure 5. For the first use of the LCSS board, it is advisable to set the gain of the built-in amplifiers to the unit value. This operation can be carried out by using a little screwdriver and an ohm-meter. The resistive trimmers R14, R15, R23, R22, R30, R31, R38, R39, have to be set at their minimum possible value by rotating their little top screw (see figure 6).

Figure 5: The red arrows indicate the two pins of J11and J13 to short-circuit.

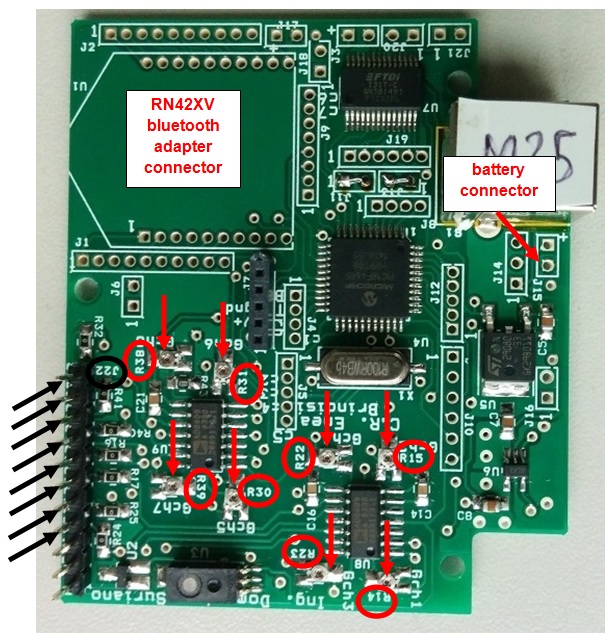
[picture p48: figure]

7

Figure 6: the black arrows and the black circle show the pins and the connector where the analog signals of the sensors have to be wired; while the red arrows and red circles indicate where the R14, R15, R23, R22, R30, R31, R38, R39 resistive trimmers are placed.

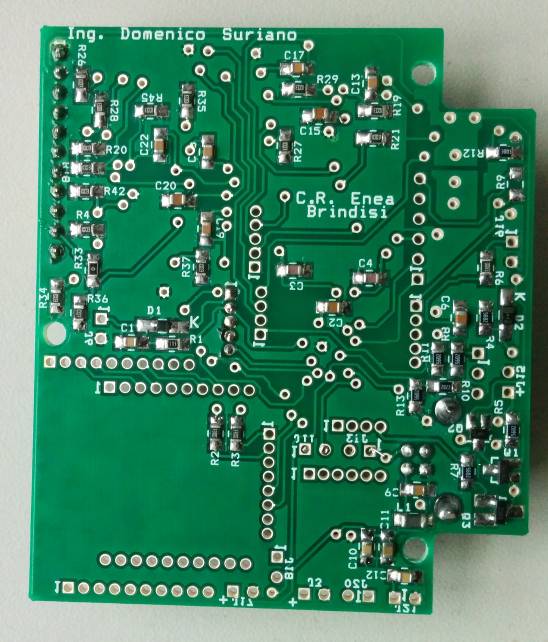
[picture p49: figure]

8

Figure 7: LCSS adapter bottom view.

The core of the LCSS adapter board is a PIC 18F4685 microcontroller by Microchip, which has to be programmed for the correct board operation. The tool needed to program the board is the "ICD2" programmer by Microchip. The necessary cable to connect the "ICD2" programmer to the LCSS board has to be assembled, as shown in figure 8. The cable is composed of an RJ11 female connector, a five positions male connector, and the wires. Optionally, the RJ11 connector can be fixed on a piece of a prototype board. The final appearance of the fully assembled cable is shown in figures 9 and 10. The electronic components needed for assembling both the LCSS adapter board and its programming cable are listed in the files placed in the subfolders "lcss adapter/bom/board" and "lcss adapter/bom/cable". In those files are also indicated the suppliers that sell all the required components. Once the programming cable and the LCSS board have been assembled, it is possible to burn the LCSS firmware on the board by using the "ICD2" programmer and the MPLAB IDE v. 8.66 distributed by Microchip (see https://www.microchip.com/development-tools/pic-and-dspic-downloads-archive (https://www.microchip.com/development-tools/pic-and-dspic-downloads-archive) ). The program to burn on the LCSS board microcontroller is the "lcss_adapter.hex", located in the subfolder "lcss_adapter/firmware". When the user is going to connect the programming cable to the J7 socket of the LCSS board, he has to be careful to insert the male connector correctly: pin n.1 of it has to be inserted in the pin n.1 of the J7 socket. All the files related to the LCSS firmware are available in the subfolder "lcss_adapter/firmware/project_files" for modifications. The code of the LCSS firmware is written in "C" language; PCH libraries distributed by CCS are required to modify and compile the source code (see: https://www.ccsinfo.com/product_info.php?products_id=PCH_full ).

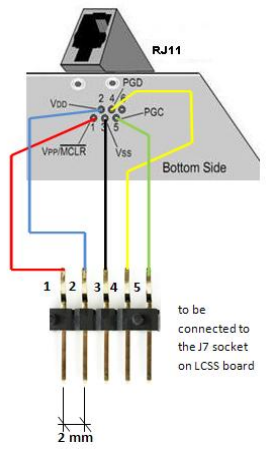
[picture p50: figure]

9

Figure 8: connections to make for assembling the cable to program the LCSS board.


Figure 9: top view of the programmer cable for LCSS board.


Figure 10: bottom view of the programmer cable for LCSS board.

## Using the ADC Pi

The second option for using analog output interface devices with SentinAir is given by mounting the ADC Pi board on SentinAir. This board is provided by ABelectronics (https://www.abelectronics.co.uk/) (see figure 11, 12) and it is based on the MCP3424 microprocessor, which is an analog-to-digital converter. The software driver for MCP3424, and therefore for the ADC Pi board, is already available in the repository of SentinAir in the folder “devices”. This board is featured by two MCP3424 microprocessors each containing four analog inputs. Therefore, the total number of signals for each ADC Pi board is eight. The maximum analog-to-digital conversion accuracy provided by MCP3424 is 17 bits. The


10

ADC Pi is attached to the Raspberry board through the Raspberry GPIO connector. This board is interfaced with the Raspberry through the I2C port. No electrical wiring is necessary to connect the ADC Pi board to Raspberry, because the power and the I2C bus connections are provided by the GPIO connector to insert directly on the Raspberry board (see figure 12).

Figure 11: ADC Pi board layout. The V1 and V2 terminals are devoted to the I2C address selection of the two MCP3424 microprocessors of the board. The jumpers of the connector on the right side of the picture set the I2c bus address of each microprocessor. The pins numbered from 1 to 10 are the analog inputs.

Figure 12: the ADC Pi connected to the Raspberry Pi through the GPIO connector.

11

## SentinAir software installation (basic procedure)

This is a quick procedure to install the SentinAir software making the minimum steps. If you desire a higher level of customization, you can refer to the “SentinAir software installation”chapter of this guide. The procedure is composed of two steps:

### a) Installing the SentinAir sd card image

Download the latest SentinAir SD card image file. (https://drive.google.com/file/d/1aCveRqDdmFK5M8jFvlvt5PZba1nvuoS0/view?usp=sharing) Write it in an SD card having at least 2 GB (4 GB recommended) of memory space by using, for example, Win32diskimage.exe program (for Windows operative systems).

### b) Enabling the use of the IMAP-SMTP module (optional)

To use the IMAP-SMTP module (see the chapters “SentinAir start up”, and “controlling SentinAir by e-mail”), please, follow the steps described in points 10 and 11 of the section “Installing the SentinAir software modules”.

## SentinAir start-up after the basic installation procedure

Supposing you have finished the a) point of the basic installation procedure, insert the SD card in the SentinAir device, plug one or more devices among the ones listed in table 1 into one of the system ports, and give power to SentinAir. After a few seconds, the green light starts blinking. Following this stage, the yellow light starts blinking. This means that the system is performing the port scanning. If one or more devices/sensors/instruments are found, the system automatically starts to acquire data (entering in the active monitoring mode and starting a new measurement session), and the yellow light turns on. To stop the measurement session, you have to use the “SentinAir user interface” and send the on-purpose command to the system (please, refer to the “Using the SentinAir user interface” chapter of this guide).

## SentinAir software installation (advanced procedure)

The procedure described below allows skilled users to customize the SentinAir system during the installation process. All the software necessary to operate a SentinAir device runs on Raspbian Stretch Lite Operative System (OS); therefore, the first step is downloading and installing it on a SentinAir device or a Raspberry 3 B+ board. For a correct SentinAir software installation, please, follow in sequence the below procedures. For the first software installation, the user has to plug a keyboard into the USB port and a monitor into the HDMI port. Subsequently, it is possible to access the system via SSH connections by using programs such as putty.exe or WinSCP.exe (for Windows operative systems).

### a) Installing Raspbian Stretch Lite operative system

1. Download the Raspbian Stretch Lite OS image into a computer from the link: https://www.raspberrypi.org/downloads/raspbian/ and flash it in an SD card memory featured by at least 2 GB of room by using, for example, Win32diskimage.exe program (for Windows operative systems).
2. Create a blank file called ssh (no extension). Save this file in the root of the MicroSD card with the flashed image. This operation is for enabling SSH connections at start-up.

12

3. In order to allow SentinAir to connect to a Wi-Fi network when it turns on, create a wpa_supplicant.conf file and write inside the following lines:

ctrl_interface=DIR=/var/run/wpa_supplicant GROUP =netdev
update_config=1
country=<your country code>
# home network; allow all valid ciphers

network={
ssid="<your network name>" scan_ssid=1
key_mgmt=WPA-PSK
psk="<your network password>"
}

Save and close the file. If you are using the Windows operative system to write the file, you have to convert it to the Linux/Unix standard. To do this, it is possible to use the program dos2unix.exe. Save wpa_supplicant.conf in the root of the MicroSD card with the flashed image.
4. Plug the Sd card in the Raspberry board and power it.
5. Find the SentinAir IP address by using programs to scan the network set in the wpa_supplicant.conf; for example, for this purpose, there is an "app" for the Android system called FindPi. Once found which is the SentinAir device IP address, it will be possible to continue the installation process by connecting to SentinAir from another computer via SSH connections. To do this, for example, it is useful the program putty.exe, if the computer has a Windows operative system running on it.

### b) Preparing Raspbian for SentinAir installation

1. Power the SentinAir device or the Raspberry 3 B+ board, log in it, and type the command: sudo raspi-config.
2. To set the device name, select Network Options/Hostname and insert the device name. It is mandatory to enter a name with a "hyphen" inside, for example, sentinair-S1. This is for the correct functioning of SentinAir software. The part of the name following the hyphen is the identity number you choose for the device. Do not exit from raspi-config yet.
3. To use the serial port for connecting devices, select Interfacing options/Serial and then press in sequence "NO" and "YES". If everything is fine, you should see the message "The serial login shell is disabled. The serial interface is enabled". Then press "OK".
4. To use I2C ports for connecting devices, select Interfacing options and then P5 I2. Select “yes” to enable the I2C ports.
5. To expand the use of the memory on your SD card, select Advanced Options/ expand Filesystem. Select then FINISH and reboot the system.
6. Run the command sudo nano /etc/hosts and update the file by modifying the line: "127.0.0.1 raspberrypi" in the line: "127.0.0.1 <device-name>", where <device-name> has to be the same name selected in the step 2 (which is, as for example sentinair-S1). Reboot the system.

13

7. To complete the configuration, we have to modify the file “/boot/config.txt”. The purpose of the serial port called /dev/ttyAMA0 has to be changed: we have to disable the Bluetooth service that uses this port and set it as a general-purpose serial port. To do this, type sudo nano /boot/config.txt, and then add at the end of the file, the row: dtoverlay=pi3-disable-bt. Moreover, we have to turn off the nuilt-in activity led and activate the green led on the panel connected to pin19 of the GPIO. To do this operation, add also the line “dtoverlay=pi3-act-led,gpio=19”. Save and close the file. After doing this, prevent Bluetooth service to use serial port by typing the command: sudo systemctl disable hciuart. Then reboot the system by running sudo reboot.
8. Update the Raspbian repository by typing the command: sudo apt-get update.
9. From now on, to perform the next steps of installation, it is needed to log into the system with the help of a keyboard and a monitor. This is necessary because the built-in Wi-Fi modem will turn in a Wi-Fi access point, and therefore it is impossible to continue while SentinAir is connected to a pre-existing Wi-Fi LAN. Moreover, to connect the device to the Internet, it is going to be necessary a USB stick modem with a valid SIM card enabled by an Internet Service Provider to connect to the Internet (for example, the model Huawey E303 does not require installation procedures). This is why the Ethernet port will be reserved to connect instruments to form a local "stand-alone" LAN. Therefore run sudo halt to stop the system, plug the USB stick modem, the keyboard, and a monitor, then log in again.
10. Download and install dnsmasq and hostapd by typing the command sudo apt-get install -y dnsmasq hostapd.
11. Stop the execution of the software just installed by running the commands: sudo systemctl stop dnsmasq and sudo systemctl stop hostapd
12. Set a static IP for the system and configure dhcpcd by opening the file dhcpcd.conf with the command sudo nano /etc/dhcpcd.conf and add at the end of the file the lines:
interface wlan0
static ip_address=192.168.4.1/24 (or an alternative IP address you choose)
nohook wpa_supplicant
dhcp-range=192.168.4.2,192.168.4.100,255.255.255.0,24h
interface eth0
static ip_address=192.168.20.1/24
static routers=192.168.20.1
nogateway
Save and close the file.
13. Configure the hostapd software by creating the file hostapd.conf , to do this, run the command sudo nano /etc/hostapd/hostapd.conf . Then insert in the file the following lines: interface=wlan0
driver=nl80211
ssid=device-name (for example: sentinair-S1)
hw_mode=g
channel=7
wmm_enabled=0
macaddr_acl=0

14

auth_algs=1
ignore_broadcast_ssid=0
wpa=2
wpa_passphrase=sentinair1
wpa_key_mgmt=WPA-PSK
wpa_pairwise=TKIP
rsn_pairwise=CCMP
Then save and close the file.
14. Complete hostapd configuration by typing sudo nano /etc/default/hostapd. Then modify the line:
#DAEMON_CONF=””

in the new line
DAEMON_CONF=”/etc/hostapd/hostapd.conf “
Save and close the file.
15. Run the command sudo nano /etc/init.d/hoastapd and replace the line DAEMON_CONF=
whit the line
DAEMON_CONF=/etc/hostapd/hostapd.conf.
Save and close the file.
16. Run the command sudo nano /etc/dnsmasq.conf and add at the end of the file the following lines:
interface=wlan0
dhcp-range=192.168.4.2,192.168.4.100,255.255.255.0,24h.
Save and close the file.
17. Finally, run the commands:
sudo systemctl restart dhcpcd.
sudo systemctl unmask hostapd sudo systemctl enable hostapd sudo systemctl start hostapd
sudo service dnsmasq start
sudo reboot

### c) Installing Lighttpd webserver

1. Install lighttpd by the command
sudo apt-get install –y lighttpd.
2. Enable the cgi-bin module of the web server by the command sudo lighty-enable-mod cgi
3. Open /etc/lighttpd/conf-available/10-cgi.conf and modify the lines:
$HTTP["url"] =~ "^/cgi-bin/" {
cgi.assign = ( "" => "" )
}
in
$HTTP["url"] =~ "^/cgi-bin/" {
alias.url += ("/cgi-bin/"=>"/var/www/cgi-bin/")

15

cgi.assign = ( "" => "" )
}
4. Run the command sudo service lighttpd force-reload
5. Create the folders: /var/www/html/data, /var/www/html/log and /var/www/html/img. Give them the read, write, and execute rights for all the users.
6. Rename the file /var/www/html/index.lighttpd.html in /var/www/html/index.lighttpd.html_. Copy the files index.html, sentinair.jpg, and btnplt.png in the folder /var/www/html/.
7. Copy the files fileinspector.py and surianocliweb.py in the folder /var/www/cgi-bin/ and give them read, write, and execution rights for all the users. Then reboot the system.

### d) Installing the SentinAir software modules

1. Install python3-serial by running the command sudo apt-get install python3-serial.
2. Install pip3 by running the command sudo apt-get install python3-pip
3. Install the library RPi.GPIO by running the command sudo apt-get install python3-RPi.GPIO.
4. Install the library libscrc by running the command sudo pip3 install libscrc.
5. Install the library smbus2 (for i2c manging) by typing the command sudo pip3 install smbus2
6. Install the library python3-matplotlib by running the command sudo apt-get install –y python3-matplotlib
7. Reboot the system.
8. Create the folder /home/pi/sentinair. SentinAir software files have to be mandatorily copied into this folder
9. Copy in /home/pi/sentinair/ the following files and folders:
- sentinair.py
- sentinair_system_manager.py
- sentinair_system_installer.py
- imap-smtp-interface.py
- imap-smtp-monitor.sh
- mail-config.sentinair
- devices
The folder "devices" is the folder where devices drivers have mandatorily to be placed.
10. In order to get started SentinAir software when the system boots, insert the following lines in the file /etc/rc.local before the line “exit 0”:
python3 /home/pi/sentinair/sentinair_system_manager.py&
WARNING: if you are editing rc.local on a Windows OS, remember to convert it in Unix/Linux format through the “dos2unix.exe” utility.
11. Open the “mail-config.sentinair” file and put your e-mail account data in the lines without the comment character (#) avoiding inserting the “space” character, like the example below: MAIL_ADDRESS="my-email_address@my_company.com" MAIL_PWD="my-email-account-password"
SMTP_SERVER="my-smtp-server-url"
IMAP_SERVER="my-imap-server-url"

16

12. Reboot the system

## Setting up SentinAir internet connection

The USB stick modem Internet plugged into one of the USB ports available gives the channel to reach a SentinAir system from the. If a Huawey E303 is used for the purpose, no installation procedures are required. Other USB stick modem models have not been tested yet. Internet Service Providers (ISP) usually do not give public IP addresses to the user; therefore, SentinAir could not be reachable from anywhere. To overcome this issue, it is possible to use the "IP tunneling" services that give the possibility to get around this hurdle. Prices of these services can vary from free to a few Euros per month. Examples of web companies offering these services are www.dataplicity.com, or www.pitunnel.com or. https:\\remote.it.

## SentinAir start-up

SentinAir gets started when the electronic hardware is powered, alternatively, by typing the command: sudo python3 /home/pi/sentinair/sentinair_system_manager.py. After few seconds the system is powered, you should see the green light asynchronous blinking, which indicates that the CPU is exchanging data with the SD memory and the system is setting up (see table 2).

Table 2: check light behaviors and their meaning
LED | LED STATUS | | MEANING
RED | OFF | System turned off
BLINKING | Sensor fault (the user must see the log file to get more information)
GREEN | ASYNCHRONOUS BLINKING | | Data exchange activity between CPU and SD memory
YELLOW | OFF | System active, monitoring not active
FAST BLINKING | | The system is performing the port scanning to find which devices are connected
SLOW BLINKING | | The shut-down procedure is going on, following the shut-down button pressing
ON | Monitoring active

When SentinAir gets started, before getting ready, it performs some preliminary operations to work appropriately. Firstly, it makes blink the yellow check light to indicate that the system is performing the scanning of the system ports to find which devices, among the ones whose driver is already installed in the system, are plugged into. When a device is found, it got connected to the system. This operation might last a few seconds, and during this time, you should see if you have a monitor plugged into the HDMI port, system messages on the screen. From now on, all the relevant operations and events are logged in the on-purpose log file of the system manager (the default name is sentinair-log.txt). During this period, the system cannot accept commands from the user; sometimes, it can last a few minutes. As soon as this operation is completed, SentinAir reads the file status.sentinair, where there is information about the device status: "standby", or "active monitoring". If the system is in "active monitoring" status, a new measurement session gets started; therefore, the yellow led check light turns on, and a new file containing the measurement data is created. The last operation of the start-up phase is the sending of an e-mail to the e-mail address indicated in the file mail-config.sentinair if the USB stick modem is plugged into the system (see


17

figure 13). In the current version of the software, SentinAir configuration is featured by a static IP on the cable Ethernet port. Devices connected to this interface will form a "stand-alone" net that is not connected to the Internet. If the user needs to connect more devices, for example, it is possible to use an Ethernet switch.

Figure 13: E-mail sent by SentinAir at start-up time.

## Installing devices drivers in SentinAir

SentinAir can read data from any device as long as the specific driver of the device is installed in the system. It is mandatory that the device driver files have to be in the folder /home/pi/sentinair/device. In order to easily install drivers, the user can log into the system by SSH connection via the Wi-Fi link through the LAN set up by SentinAir. Then the user has to use the module sentinair_system_installer.py by opening it through the command:
sudo python3 /home/pi/sentinair/sentinair_system_installer.py.
Once opened the installer, the commands available are listed in table 3.

18

Table 3: commands available for the SentinAir system installer
Command function | Command syntax | Example | Effect
Device driver installation | i,device_name.py | i,pms3003.py | Installs the driver for the device pms3003
Device driver uninstalling | u,device_name.py | u,pms3003.py | Uninstalls the driver for the device pms3003
Checking the current drivers installed | c | c | Displays a list of the drivers currently installed
Modifying the current path of the system manager module | m | m | Writes in the file "manager_dir.sentinair" the new path of the manager system module
Asking for the commands list available | h | h | Displays a brief manual where are shown the commands
Quit the program | q | q | Quits the programs

An example of sentinair_system_installer.py use is shown in figure 14. After updating the system with new installations, it has to be rebooted or restarted.


19

Figure 14: the installer user interface

## Using the SentinAir user interface

SentinAir system main interface is provided by the sentinair.py module. The user has to log into the system by SSH connection via the Wi-Fi link through the LAN set up by SentinAir. To open the SentinAir user interface, type the command:
python3 /home/pi/sentinair/sentinair.py.
Once opened the user interface, the commands available are listed in table 4.

20

Table 4: commands available for the SentinAir user interface
Command function | Command syntax | Example | Effect
Starting a new monitoring session | s,seconds | s,60 | A new monitoring session gets started. Every 60 seconds, device measurements data are read and stored in a file
Stopping a measurement session | b | b | Stops the current measurement session
Retrieving information about the system status | | | | i | i | Displays information such as the devices currently connected to the system, the sampling rate of the measurement session, or if the system is on standby.
Retrieving information about the devices connected to the system | | | c | c | The system returns the information about the connected devices: identity, units of measurements, current measurements
Asking for the commands list available | | h | h | Displays a brief manual where are shown the commands
Scanning the ports and connecting the devices plugged into SentinAir | ports | | s | s | The system scans all the ports (USB, Ethernet, etc.) and recognizes if one of the installed devices is | plugged into
Quit the program | | | q | q | Quits the programs

An example of the use of the SentinAir user interface is shown in figure 15. If the system is not in active monitoring mode (you can see this by checking the yellow light, which should be off), the message “No measurement session ongoing” is shown. If you want to start acquiring data from sensors (putting the system in active monitoring mode), you have to type the command “s,60”. This way a monitoring session will start at 60 second sampling rate and the yellow check light will turn on.


21

Figure 15: the SentinAir user interface.

## Controlling SentinAir by e-mail

SentinAir has been designed for being used in all that cases where it is necessary to perform experiments or measurements in remote areas, where possibly the internet link is weak or unstable, and therefore, where it is difficult the remote control and the data download from the device. For this purpose, commands and data can be exchanged by e-mail sending and receiving. SentinAir checks periodically on the IMAP server configured in the imap-smtp-interface.py for the presence of e-mails containing commands, and when the radio signal allows it, sends back the response. The imap-smtp-interface.py module is optional, and it is not essential for SentinAir operation. If it is present, it is launched by sentinair_system_manager.py at start-up. The user can send commands through e-mail for both the SentinAir system or for the operative system programs and services. A


22

typical SentinAir command is, for example, "s,60", which causes the start of a new measurement session at 60 seconds sampling rate. A command directed for the operative system could be, for example, "ls –l", which returns the list of files and directories contained in the current system directory. E-mails containing commands for the operative system must have as subject the text: "device_ID system command",
where the "device_ID" is the part of the device name which follows the hyphen. For example: if the device name was set as "sentinair-S1" during the software installation process, then the device_ID will be "S1" (see figure 16 and 17). Moreover, e-mails containing commands directed to SentinAir software must have as subject the text:
"device_ID SentinAir command" (please, mind the correct case of letters).
The body of the e-mail must have a line where there is "do: command". For example: "do: s,60" (please, mind the "space" character between "do:" and the command). It is possible to download every kind of file present in the device by sending an e-mail having the subject as: "device_ID system command", and the body having the line as: "do: fget /path_of_the_file/file_to_download" (mind the space characters between "do:" and "fget" and between "fget" and "/path_of_the_file/file_to_download"). For example: "do: fget /var/www/html/log/sentinair-log.txt".

Figure 16: e-mail sent to SentinAir containing a command for the operative system

Figure 17: -mail sent to SentinAir containing a command for SentinAir system


23

## SentinAir operations featuring the measurement session

When a new measurement session gets started (for example, by the command "s,60"), the yellow led check light turns on. Three new files are created: the file containing the records of the measurements along with the timestamps (see figure 18) and named: "device_name_date_time.txt" (for example sentinair-S1_2020-02-03_09-30-15.txt), the file containing hourly averages of measurement and named: "device_name_date_time_hourlymeans.txt" (for example: "sentinair-S1_2020-02-03_09-30-15_hourlymeans.txt"), and the file containing the daily averages of the measurements, named: "device_name_date_time_dailymeans.txt" (for example: "sentinair-S1_2020-02-03_09-30-15_dailymeans.txt"). Hourly and daily averages are computed in real-time by the module sentinair_system_manager.py, and they are stored in the path indicated in that module (which is for default: "/var/www/html/data"). Another operation performed by the sentinair_system_manager.py module during the measurement session is the plotting of each magnitude measured by each of the devices connected to SentinAir. The plots are stored in jpg files placed in the path "/var/www/html/img" (which is their default path). Those files are encapsulated in web pages and served to the user when he connects by a web browser to SentinAir.

Figure 18: a file containing records of a SentinAir measurement session.

## SentinAir web pages

The user can monitor SentinAir activity by connecting through a web browser to SentinAir (see figure 19). As for the other user interfaces given by the sentinair.py module and the sentinair_system_installer.py module, the webserver of SentinAir can be reached by connecting through a Wi-Fi link at the address set in the /etc/dhcpcd.conf file (which default is 192.168.4.1), or through internet connections via the selected "IP tunneling" service. Web pages of SentinAir allow the user to download all data and log files that are in the system.


24

Figure 19: web pages from SentinAir

## Shutting down SentinAir

To shut down the system through the button shown in figure 4, the user has to press it and hold it pressed until the yellow light starts blinking. At that moment, it is possible to release the button. Before taking off the power from the system, you have to wait that the yellow light stops blinking and after that, wait the green light stops blinking and the red light turns off. Optionally, you have to type the “sudo halt” command to the operative system running on the Raspberry board to properly shut-down the system.

## How to write device drivers for SentinAir

The creation of new device drivers for SentinAir is highly expected. It is desirable that researchers, or users, write drivers for their own devices to use with the SentinAir system. In order to facilitate this task, driver templates have been written and stored in the folder “devices/device-driver-templates” of the SentinAir Github repository. (https://github.com/domenico-suriano/SentinAir) When a new driver is going to be written, the user must follow some rules in order to get it fully compatible and operating with the pre-existing software. Some of these rules are common to all types of devices (USB, serial, I2C, Ethernet), while there are rules specific for each type of sensor/device. We recall that sensors or devices featured by analog output interfaces must be used with the LCSS adapter board (having a USB output interface), or with the ADC Pi (having an I2C output interface). A good way to getting started with writing new device drivers is by modifying the template file related to your device type (“ethernet-device-template.py”, “usb-device-template.py”, “serial-device-template.py”, or “i2c-device-template.py”).
Here below it is shown a step by step procedure which hopefully will help the user to correctly write new device drivers. In doing this, we will report some examples referring to the files of some

25

drivers already developed (“nox405.py”, ” ac32.py”, ”bh1750.py”), and to the files of the driver templates.
1. Import the necessary library. For I2C devices, “smsbus2” is mandatory (see “bh1750.py” and “i2c-device-template.py”), for USB and serial devices “serial” is mandatory (see “nox405.py” and “serial-device-template.py”), for Ethernet devices “socket” is mandatory (see ” ac32.py” and “ethernet-device-template.py”). Also import other libraries specific for your device operation (see for example “time” and “_thread” in “nox405.py”)
2. Set the mandatory constant strings CONNECTION_TYPE, DEVICE_IDENTITY, and DEVICE_SENSORS common for all the device types following the indications in the driver template files (“ethernet-device-template.py”, “usb-device-template.py”, “serial-device-template.py”, or “i2c-device-template.py”). The DEVICE_SENSORS string contains the magnitude names measured by the device, separated by a semicolon character; for example (see “nox405.py”): "no2[ppb];no[ppb];nox[ppb]". Then set the constants specific for each type of device: I2C_ADDRESSES, which must be a Python list of integer values (for I2C devices, see “bh1750.py” and “i2c-device-template.py”), ETH_ADDRESSES, which must be a list of strings (for Ethernet devices, see ” ac32.py” and “ethernet-device-template.py”), DEVICE_BAUD_RATE, which must be an integer value (for serial and usb devices, see “nox405.py” and “serial-device-template.py”). Set the other constants (if any) specific for your device operation.
3. Create the device class name. It is mandatory that the class name must be the same as the driver file name with the first letter capitalized. For example: the driver “nox405.py” contains the class Nox405.
4. In the “__init(self)” method of the device class, you can find the mandatory variables common for all the device types:
self.identity = DEVICE_IDENTITY
self.connection_type = CONNECTION_TYPE
self.sensors = DEVICE_SENSORS.
There are also variables specific for a device type. For I2C device (see “bh1750.py” and “i2c-device-template.py”), you will find:
self.addresses = I2C_ADDRESSES
self.device_address = 0x00.
For Ethernet devices you will find (see ” ac32.py” and “ethernet-device-template.py”): self.addresses = ETH_ADDRESSES
self.device_address = None
self.sk = None
For serial or usb devices you will find (see “nox405.py” and “serial-device-template.py”): self.baud_rate = DEVICE_BAUD_RATE
self.portname = ""
self.port = None.
The user must not modify the above-mentioned lines, but he can add variables necessary and specific for his device operation (see, for example, the “__init(self)” method in the file “nox405.py”).

26

5. The device class must contain the following methods common for all the device types; they are:
def getConnectionType(self):
return self.connection_type def getIdentity(self):
return self.identity
def getSensors(self):
return self.sensors
def setIdentity(self,idstring):
self.identity = idstring
Moreover, for a specific device type, there are other mandatory methods. For I2C devices device (see “bh1750.py” and “i2c-device-template.py”), we have:
def getConnectionParams(self):
return self.addresses
def terminate(self):
self.device_address = 0x00.
For Ethernet devices (see ” ac32.py” and “ethernet-device-template.py”), we have: def getConnectionParams(self):
return self.addresses
def terminate(self):
try:
self.sk.close()
except:
return
def __del__(self):
try:
self.sk.close()
except:
return
For usb or serial devices (see “nox405.py” and “serial-device-template.py”), we have: def getConnectionParams(self):
return [self.portname,self.baud_rate]
def terminate(self):
try:
self.port.close()
except:
return
def __del__(self):
try:
self.port.close()
except:
return.

27

The user must not modify the above-listed methods, but he can add other ones specific for his device operation (see, for example, the “nox405.py”, ” ac32.py”, “bh1750.py”).
6. The class must have the method called “connect(self,address)” in case of I2C or Ethernet devices, or “connect(self,portname)” in case of serial or usb devices. This method detects if the device is connected and finds the connection parameters, for example, if it is searching for an Ethernet or I2C device, it finds the device address; or, if it is searching for a USB or serial device, it finds the USB port. If no device is found, it returns the "0" value, otherwise, it returns "1". For implementing the "connect" method, I suggest to request data from the device and see if it responds. If this operation succeeds, it means that the device is correctly connected, and in this case, the 1 value will be returned (see, for example, the “nox405.py”, ” ac32.py”, “bh1750.py”).
7. The device class must have the method "sample(self)" that must return a string containing the last measurements separated by a semicolon mark. An example of a string returned by this method could be: “27,76;0,1234;456,9”. It is mandatory that the fields contained in the string must be in the same number as the ones set in the DEVICE_SENSORS string. For example: if DEVICE_SENSORS=“no2[ppb];no[ppb];nox[ppb]” (see “nox405.py”), then the "sample(self)" method must return “27,76;0,1234;456,9".

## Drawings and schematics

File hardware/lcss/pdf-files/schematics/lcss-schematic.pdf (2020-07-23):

- J3

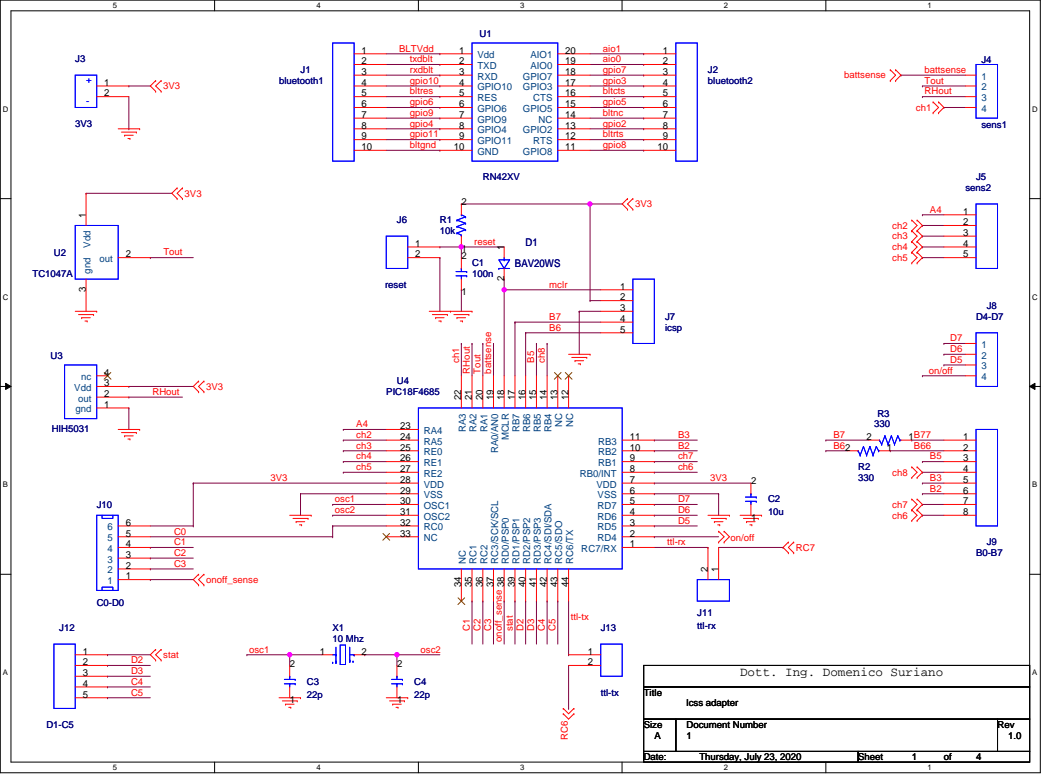
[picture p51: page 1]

Dott. Ing. Domenico Suriano

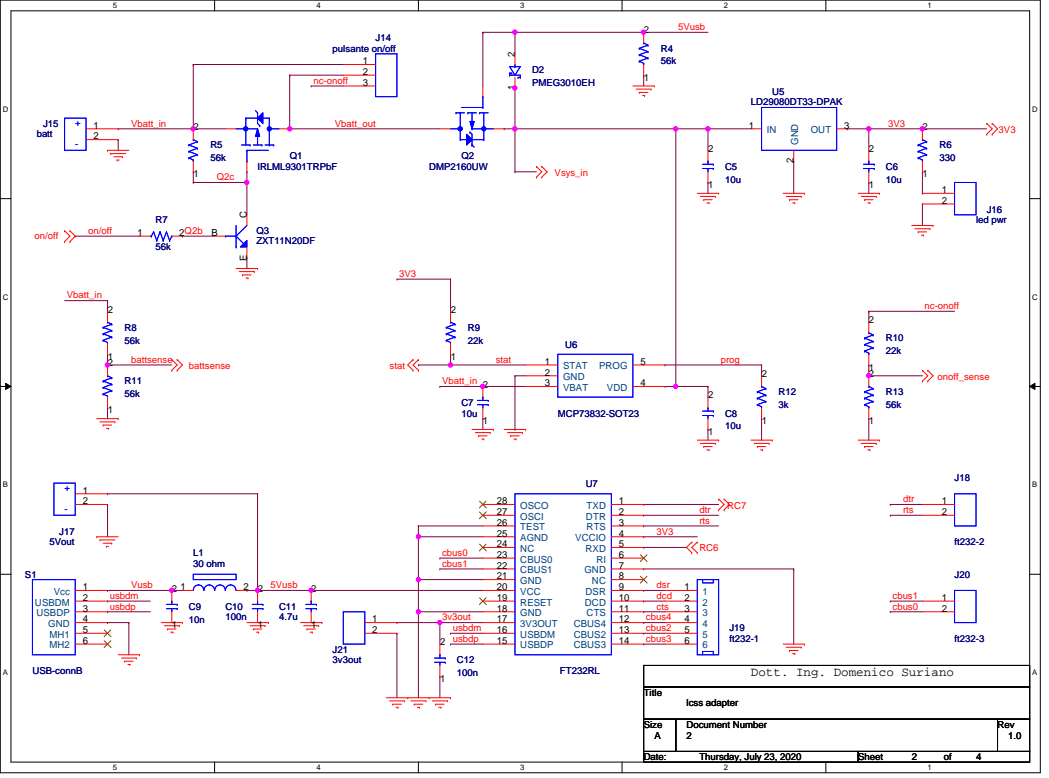
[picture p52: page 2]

CBUS3 14 USBDP 15 USBDM 16 3V3OUT 17 GND 18 RESET 19 VCC 20 GND 21 CBUS1 22 CBUS0 23 NC 24 AGND 25 TEST 26 OSCI 27 OSCO 28

Dott. Ing. Domenico Suriano

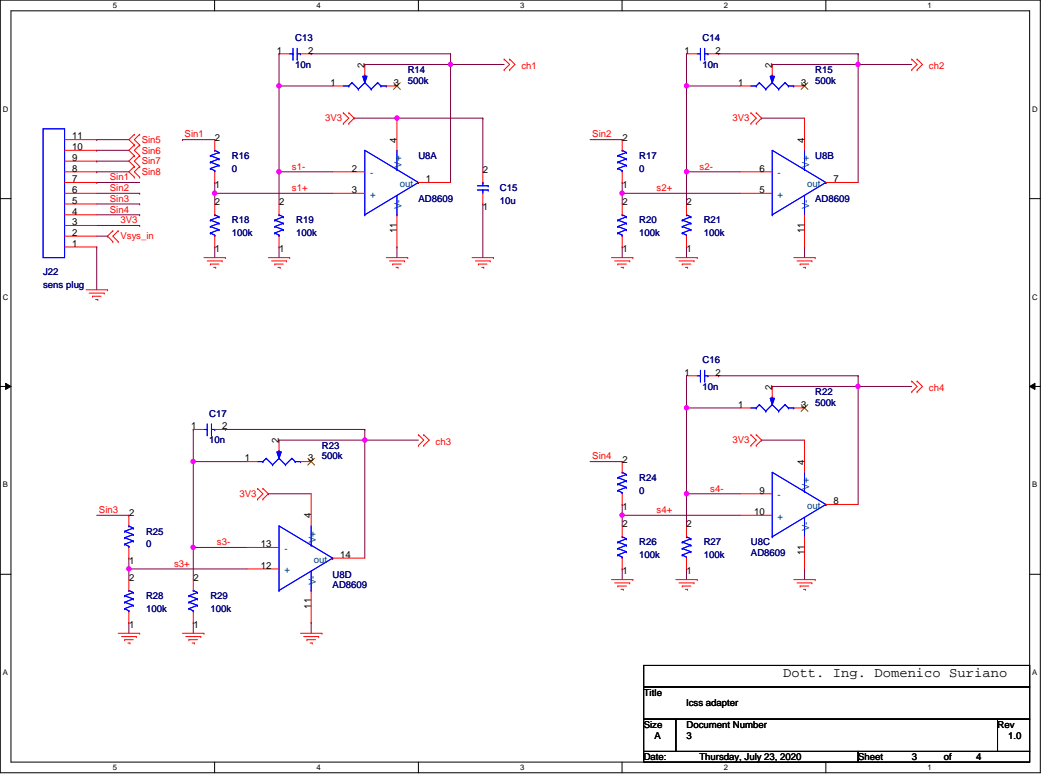
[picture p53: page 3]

Dott. Ing. Domenico Suriano

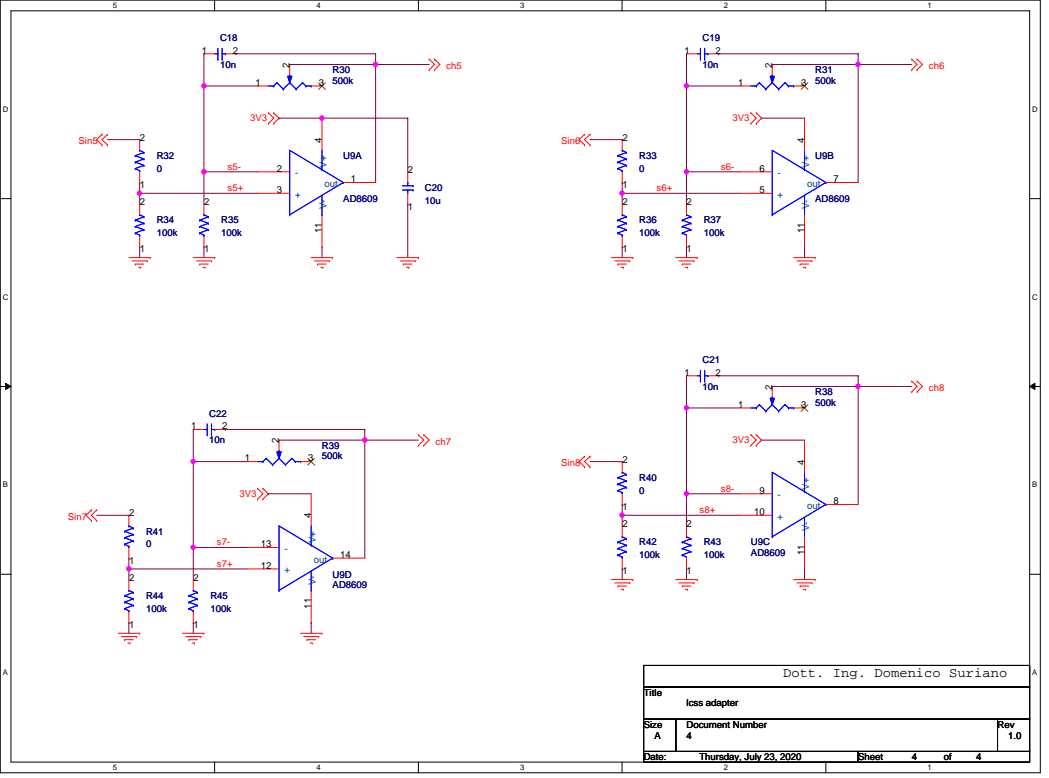
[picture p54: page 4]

Dott. Ing. Domenico Suriano

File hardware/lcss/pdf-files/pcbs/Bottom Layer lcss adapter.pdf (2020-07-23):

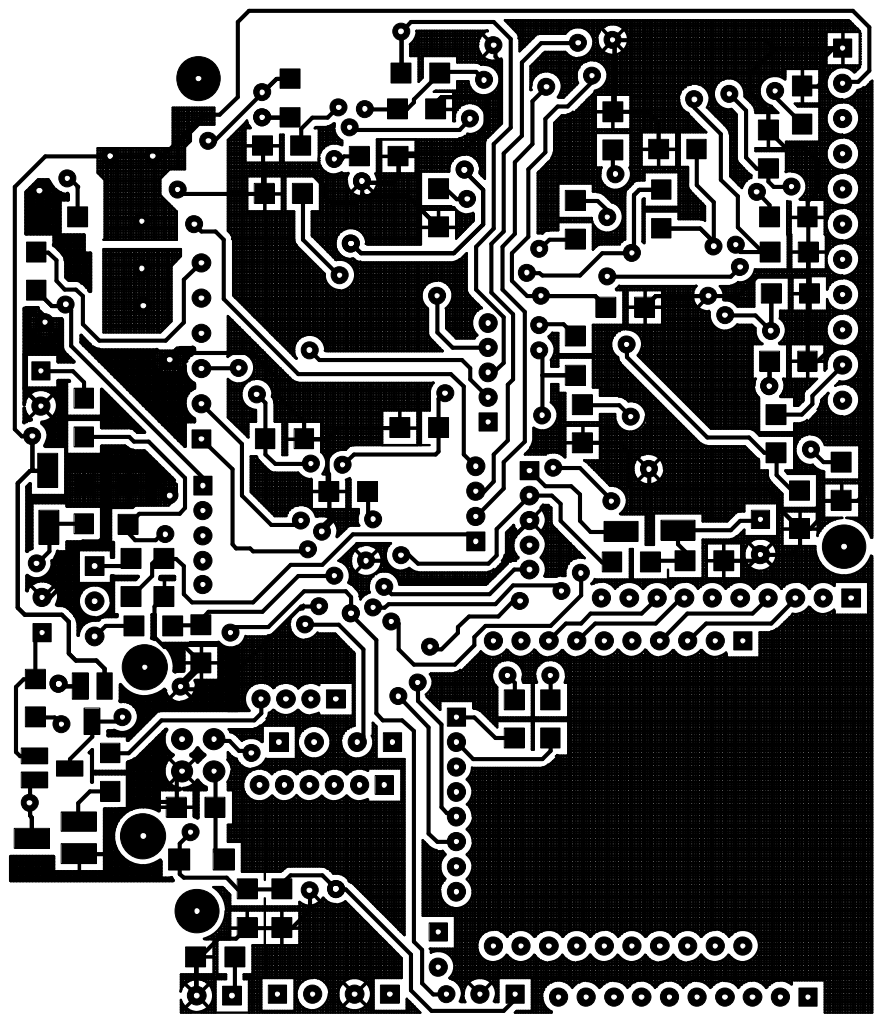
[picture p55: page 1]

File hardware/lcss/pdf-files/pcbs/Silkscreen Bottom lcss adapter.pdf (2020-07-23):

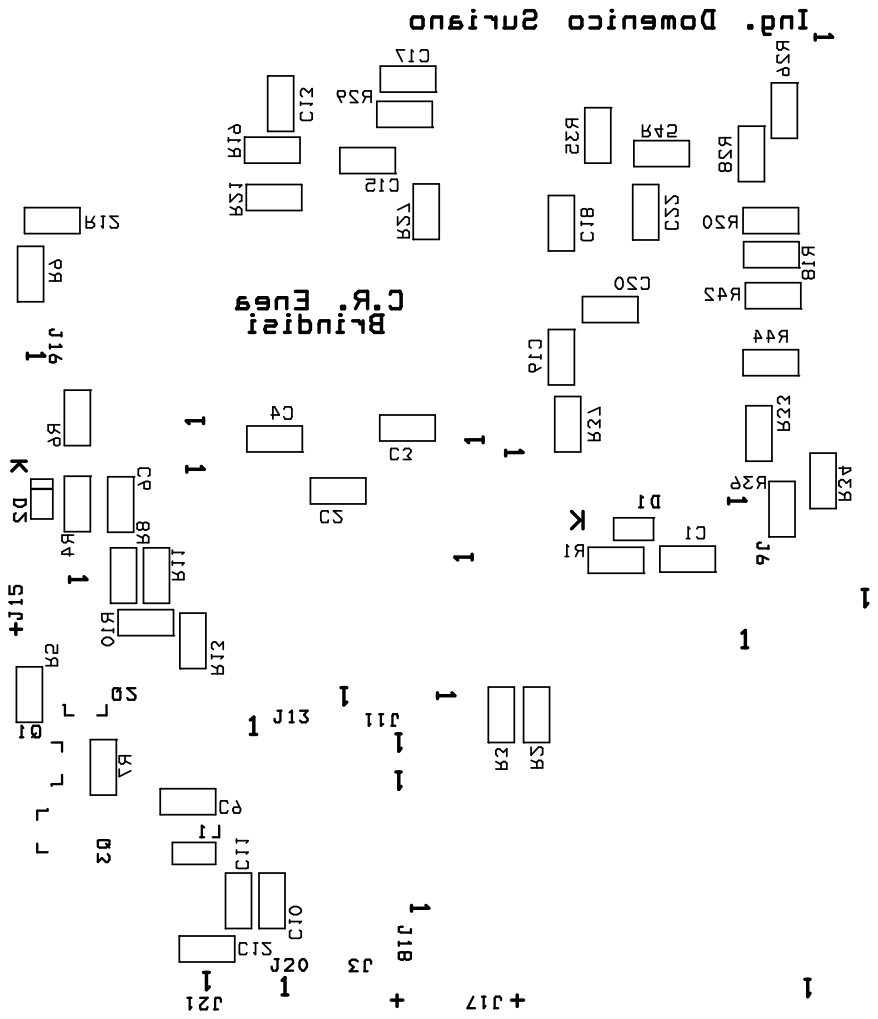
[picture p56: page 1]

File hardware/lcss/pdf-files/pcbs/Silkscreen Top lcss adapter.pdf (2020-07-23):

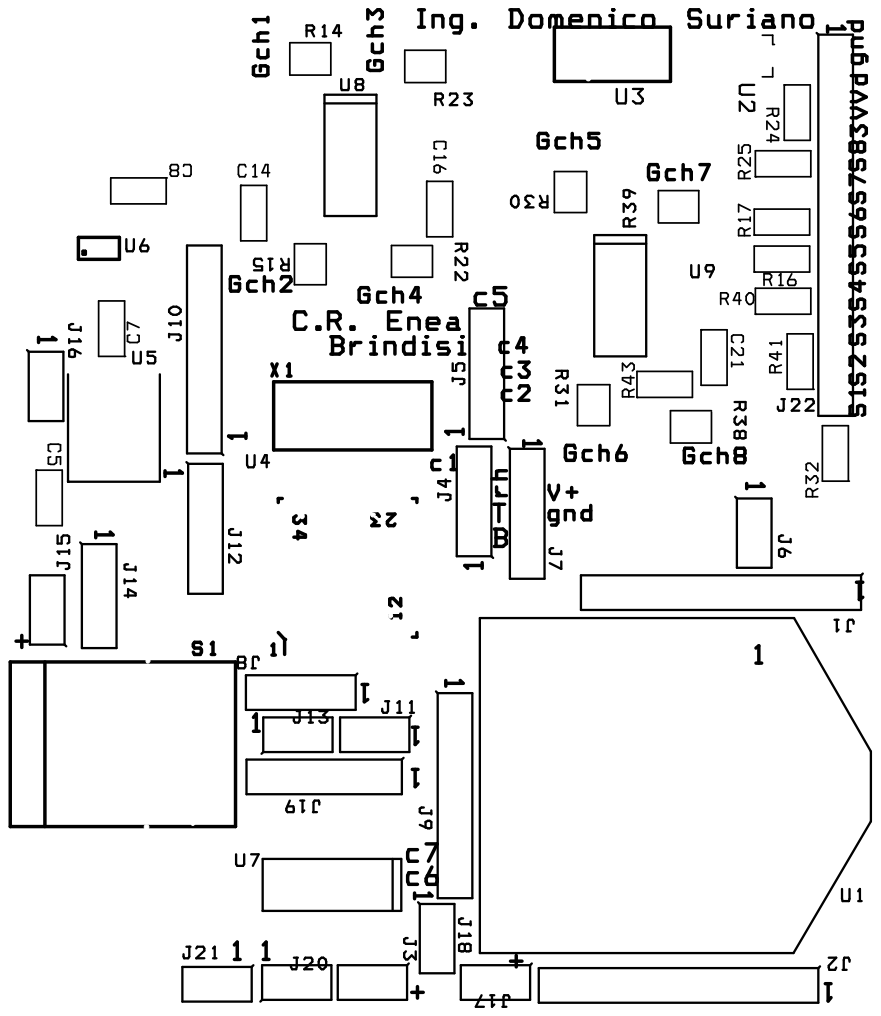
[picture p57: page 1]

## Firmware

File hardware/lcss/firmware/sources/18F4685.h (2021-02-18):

//////// Standard Header file for the PIC18F4685 device ////////////////
#device PIC18F4685
#nolist
//////// Program memory: 49152x16  Data RAM: 3328  Stack: 31
//////// I/O: 36   Analog Pins: 11
//////// Data EEPROM: 1024
//////// C Scratch area: 00   ID Location: 200000
//////// Fuses: LP,XT,HS,RC,EC,EC_IO,H4,RC_IO,PROTECT,NOPROTECT
//////// Fuses: BROWNOUT_NOSL,BROWNOUT_SW,NOBROWNOUT,BROWNOUT,WDT1,WDT2,WDT4
//////// Fuses: WDT8,WDT16,WDT32,WDT64,WDT128,WDT,NOWDT,BORV20,BORV27,BORV42
//////// Fuses: BORV45,PUT,NOPUT,CPD,NOCPD,NOSTVREN,STVREN,NODEBUG,DEBUG
//////// Fuses: NOLVP,LVP,WRT,NOWRT,WRTD,NOWRTD,IESO,NOIESO,FCMEN,NOFCMEN
//////// Fuses: PBADEN,NOPBADEN,BBSIZ1K,BBSIZ2K,WRTC,NOWRTC,WRTB,NOWRTB,EBTR
//////// Fuses: NOEBTR,EBTRB,NOEBTRB,CPB,NOCPB,LPT1OSC,NOLPT1OSC,MCLR,NOMCLR
//////// Fuses: XINST,NOXINST,INTRC,INTRC_IO,WDT256,WDT512,WDT1024,WDT2048
//////// Fuses: WDT4096,WDT8192,WDT16384,WDT32768,BBSIZ4K,RC,BBSIZ4K
//////// 
////////////////////////////////////////////////////////////////// I/O
// Discrete I/O Functions: SET_TRIS_x(), OUTPUT_x(), INPUT_x(),
//                         PORT_x_PULLUPS(), INPUT(),
//                         OUTPUT_LOW(), OUTPUT_HIGH(),
//                         OUTPUT_FLOAT(), OUTPUT_BIT()
// Constants used to identify pins in the above are:

#define PIN_A0  31744
#define PIN_A1  31745
#define PIN_A2  31746
#define PIN_A3  31747
#define PIN_A4  31748
#define PIN_A5  31749
#define PIN_A6  31750
#define PIN_A7  31751

#define PIN_B0  31752
#define PIN_B1  31753
#define PIN_B2  31754
#define PIN_B3  31755
#define PIN_B4  31756
#define PIN_B5  31757
#define PIN_B6  31758
#define PIN_B7  31759

#define PIN_C0  31760
#define PIN_C1  31761
#define PIN_C2  31762
#define PIN_C3  31763
#define PIN_C4  31764
#define PIN_C5  31765
#define PIN_C6  31766
#define PIN_C7  31767

#define PIN_D0  31768
#define PIN_D1  31769
#define PIN_D2  31770
#define PIN_D3  31771
#define PIN_D4  31772
#define PIN_D5  31773
#define PIN_D6  31774
#define PIN_D7  31775

#define PIN_E0  31776
#define PIN_E1  31777
#define PIN_E2  31778
#define PIN_E3  31779

////////////////////////////////////////////////////////////////// Useful defines
#define FALSE 0
#define TRUE 1

#define BYTE int8
#define BOOLEAN int1

#define getc getch
#define fgetc getch
#define getchar getch
#define putc putchar
#define fputc putchar
#define fgets gets
#define fputs puts

////////////////////////////////////////////////////////////////// Control
// Control Functions:  RESET_CPU(), SLEEP(), RESTART_CAUSE()
// Constants returned from RESTART_CAUSE() are:

#define WDT_TIMEOUT       7    
#define MCLR_FROM_SLEEP  11    
#define MCLR_FROM_RUN    15    
#define NORMAL_POWER_UP  12    
#define BROWNOUT_RESTART 14    
#define WDT_FROM_SLEEP   3     
#define RESET_INSTRUCTION 0    
////////////////////////////////////////////////////////////////// Timer 0
// Timer 0 (AKA RTCC)Functions: SETUP_COUNTERS() or SETUP_TIMER_0(),
//                              SET_TIMER0() or SET_RTCC(),
//                              GET_TIMER0() or GET_RTCC()
// Constants used for SETUP_TIMER_0() are:
#define T0_INTERNAL   0
#define T0_EXT_L_TO_H 32
#define T0_EXT_H_TO_L 48

#define T0_DIV_1      8
#define T0_DIV_2      0
#define T0_DIV_4      1
#define T0_DIV_8      2
#define T0_DIV_16     3
#define T0_DIV_32     4
#define T0_DIV_64     5
#define T0_DIV_128    6
#define T0_DIV_256    7

#define T0_OFF        0x80  

#define T0_8_BIT      0x40  

#define RTCC_INTERNAL   0      // The following are provided for compatibility
#define RTCC_EXT_L_TO_H 32     // with older compiler versions
#define RTCC_EXT_H_TO_L 48
#define RTCC_DIV_1      8
#define RTCC_DIV_2      0
#define RTCC_DIV_4      1
#define RTCC_DIV_8      2
#define RTCC_DIV_16     3
#define RTCC_DIV_32     4
#define RTCC_DIV_64     5
#define RTCC_DIV_128    6
#define RTCC_DIV_256    7
#define RTCC_OFF        0x80  
#define RTCC_8_BIT      0x40  

// Constants used for SETUP_COUNTERS() are the above
// constants for the 1st param and the following for
// the 2nd param:

////////////////////////////////////////////////////////////////// WDT
// Watch Dog Timer Functions: SETUP_WDT() or SETUP_COUNTERS() (see above)
//                            RESTART_WDT()
// WDT base is 4ms
//
#define WDT_ON        0x100
#define WDT_OFF       0

////////////////////////////////////////////////////////////////// Timer 1
// Timer 1 Functions: SETUP_TIMER_1, GET_TIMER1, SET_TIMER1
// Constants used for SETUP_TIMER_1() are:
//      (or (via |) together constants from each group)
#define T1_DISABLED         0
#define T1_INTERNAL         0x85
#define T1_EXTERNAL         0x87
#define T1_EXTERNAL_SYNC    0x83

#define T1_CLK_OUT          8

#define T1_DIV_BY_1         0
#define T1_DIV_BY_2         0x10
#define T1_DIV_BY_4         0x20
#define T1_DIV_BY_8         0x30

////////////////////////////////////////////////////////////////// Timer 2
// Timer 2 Functions: SETUP_TIMER_2, GET_TIMER2, SET_TIMER2
// Constants used for SETUP_TIMER_2() are:
#define T2_DISABLED         0
#define T2_DIV_BY_1         4
#define T2_DIV_BY_4         5
#define T2_DIV_BY_16        6

////////////////////////////////////////////////////////////////// Timer 3
// Timer 3 Functions: SETUP_TIMER_3, GET_TIMER3, SET_TIMER3
// Constants used for SETUP_TIMER_3() are:
//      (or (via |) together constants from each group)
#define T3_DISABLED         0
#define T3_INTERNAL         0x85
#define T3_EXTERNAL         0x87
#define T3_EXTERNAL_SYNC    0x83

#define T3_DIV_BY_1         0
#define T3_DIV_BY_2         0x10
#define T3_DIV_BY_4         0x20
#define T3_DIV_BY_8         0x30

// OR in one of the following to use timer 3 with a CCP unit
#define  T3_CCP1_TO_2  0x48
#define  T3_CCP2       0x8

////////////////////////////////////////////////////////////////// CCP
// CCP Functions: SETUP_CCPx, SET_PWMx_DUTY
// CCP Variables: CCP_x, CCP_x_LOW, CCP_x_HIGH
// Constants used for SETUP_CCPx() are:
#define CCP_OFF                         0
#define CCP_CAPTURE_FE                  4
#define CCP_CAPTURE_RE                  5
#define CCP_CAPTURE_DIV_4               6
#define CCP_CAPTURE_DIV_16              7
#define CCP_COMPARE_SET_ON_MATCH        8
#define CCP_COMPARE_CLR_ON_MATCH        9
#define CCP_COMPARE_INT                 0xA
#define CCP_COMPARE_INT_AND_TOGGLE      0x2       
#define CCP_COMPARE_RESET_TIMER         0xB
#define CCP_PWM                         0xC
#define CCP_PWM_PLUS_1                  0x1c
#define CCP_PWM_PLUS_2                  0x2c
#define CCP_PWM_PLUS_3                  0x3c
//#define CCP_USE_TIMER3                0x100  OBSOLETE, SEE TIMER-3     
#word   CCP_1    =                      getenv("SFR:CCPR1L")
#byte   CCP_1_LOW=                      getenv("SFR:CCPR1L")
#byte   CCP_1_HIGH=                     getenv("SFR:CCPR1H")
// The following should be used with the ECCP unit only (or these in)
#define CCP_PWM_H_H                     0x0c
#define CCP_PWM_H_L                     0x0d
#define CCP_PWM_L_H                     0x0e
#define CCP_PWM_L_L                     0x0f

#define CCP_PWM_FULL_BRIDGE             0x40
#define CCP_PWM_FULL_BRIDGE_REV         0xC0
#define CCP_PWM_HALF_BRIDGE             0x80

#define CCP_SHUTDOWN_ON_COMP1           0x100000
#define CCP_SHUTDOWN_ON_COMP2           0x200000
#define CCP_SHUTDOWN_ON_COMP            0x300000
#define CCP_SHUTDOWN_ON_INT0            0x400000
#define CCP_SHUTDOWN_ON_COMP1_INT0      0x500000
#define CCP_SHUTDOWN_ON_COMP2_INT0      0x600000
#define CCP_SHUTDOWN_ON_COMP_INT0       0x700000

#define CCP_SHUTDOWN_AC_L               0x000000
#define CCP_SHUTDOWN_AC_H               0x040000
#define CCP_SHUTDOWN_AC_F               0x080000

#define CCP_SHUTDOWN_BD_L               0x000000
#define CCP_SHUTDOWN_BD_H               0x010000
#define CCP_SHUTDOWN_BD_F               0x020000

#define CCP_SHUTDOWN_RESTART            0x80000000

#word   CCP_2    =                      getenv("SFR:CCPR2L")
#byte   CCP_2_LOW=                      getenv("SFR:CCPR2L")
#byte   CCP_2_HIGH=                     getenv("SFR:CCPR2H")
////////////////////////////////////////////////////////////////// PSP
// PSP Functions: SETUP_PSP, PSP_INPUT_FULL(), PSP_OUTPUT_FULL(),
//                PSP_OVERFLOW(), INPUT_D(), OUTPUT_D()
// PSP Variables: PSP_DATA
// Constants used in SETUP_PSP() are:
#define PSP_ENABLED                     0x10
#define PSP_DISABLED                    0

#byte  PSP_DATA=    0xF83               

////////////////////////////////////////////////////////////////// SPI
// SPI Functions: SETUP_SPI, SPI_WRITE, SPI_READ, SPI_DATA_IN
// Constants used in SETUP_SPI() are:
#define SPI_MASTER       0x20
#define SPI_SLAVE        0x24
#define SPI_L_TO_H       0
#define SPI_H_TO_L       0x10
#define SPI_CLK_DIV_4    0
#define SPI_CLK_DIV_16   1
#define SPI_CLK_DIV_64   2
#define SPI_CLK_T2       3
#define SPI_SS_DISABLED  1

#define SPI_SAMPLE_AT_END 0x8000
#define SPI_XMIT_L_TO_H  0x4000

////////////////////////////////////////////////////////////////// UART
// Constants used in setup_uart() are:
// FALSE - Turn UART off
// TRUE  - Turn UART on
#define UART_ADDRESS           2
#define UART_DATA              4
#define UART_AUTODETECT        8
#define UART_AUTODETECT_NOWAIT 9
#define UART_WAKEUP_ON_RDA     10
#define UART_SEND_BREAK        13
////////////////////////////////////////////////////////////////// COMP
// Comparator Variables: C1OUT, C2OUT
// Constants used in setup_comparator() are:
#define D1_D0_D3_D0  0x0Bff04
#define D1_D0_D3_D2_OUT_ON_E1_E2  0x0FF903
#define D1_D0_D3_D0_OUT_ON_E1_E2  0x0BF905
#define NC_NC_NC_NC  0x00ff07
#define D1_D0_D3_D2  0x0Fff02
#define D1_D0_NC_NC_OUT_ON_E1  0x03FD01
#define D1_VR_D3_VR 0x0Aff06
#define D0_VR_D2_VR 0x05ff0e
#define CP1_INVERT  0x0000010
#define CP2_INVERT  0x0000020

#bit C1OUT = 0xfb4.6
#bit C2OUT = 0xfb4.7

////////////////////////////////////////////////////////////////// VREF
// Constants used in setup_vref() are:
//
#define VREF_LOW  0xa0
#define VREF_HIGH 0x80
// Or (with |) the above with a number 0-15
#define VREF_F5   0x40
#define VREF_COMP 0x10

////////////////////////////////////////////////////////////////// VREF
// Constants used in setup_low_volt_detect() are:
//
#define LVD_LVDIN   0x1F
#define LVD_45 0x1E
#define LVD_42 0x1D
#define LVD_40 0x1C
#define LVD_38 0x1B
#define LVD_36 0x1A
#define LVD_35 0x19
#define LVD_33 0x18
#define LVD_30 0x17
#define LVD_28 0x16
#define LVD_27 0x15
#define LVD_25 0x14
#define LVD_24 0x13
#define LVD_23 0x12
#define LVD_22 0x11
#define LVD_21 0x10

#define LVD_TRIGGER_BELOW 0
#define LVD_TRIGGER_ABOVE 0x80


////////////////////////////////////////////////////////////////// INTERNAL RC
// Constants used in setup_oscillator() are:
// First param:
#define OSC_31KHZ   0
#define OSC_125KHZ  0x10
#define OSC_250KHZ  0x20
#define OSC_500KHZ  0x30
#define OSC_1MHZ    0x40
#define OSC_2MHZ    0x50
#define OSC_4MHZ    0x60
#define OSC_8MHZ    0x70
#define OSC_16MHZ   0x4060
#define OSC_32MHZ   0x4070
// The following may be OR'ed in with the above using |
#define OSC_TIMER1  1
#define OSC_INTRC   2
#define OSC_NORMAL  0
// The following may be OR'ed in with the above using |
#define OSC_IDLE_MODE  0x80
#define OSC_31250   0x8000
#define OSC_PLL_ON  0x4000
#define OSC_PLL_OFF 0
// A second optional parameter may be used with this part to fine
// tune the speed (signed int,0-31)
// Result may be (ignore all other bits)
#define OSC_STATE_STABLE 4
#define OSC_STATE_EXT_RUNNING 8
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

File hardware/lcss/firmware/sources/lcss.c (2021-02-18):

//creato il 14/3/2018
#include <18F4685.h>
#device ADC=16 //RISOLUZIONE ADC
#fuses HS,NOWDT,NOPROTECT,NOLVP,BROWNOUT
#use delay(clock=10M)
#use rs232(baud=115200, xmit=PIN_C6, rcv=PIN_C7, timeout = 1500, errors, stream=usb)

#include "C:\progetti\firmware-multisensori\sensori.h"

#define IDENTITY "LCSS\r\n"
#define BUFFER_LENGHT 10

static byte buffer_index;
static byte buffer_counter;
static byte usb_buffer_pointer;
static BYTE usb_rx_buf[BUFFER_LENGHT];

static float misure[11];

////////////////////////////////////////////////////////////////////////////
////// FORMATO PACCHETTI IN USCITA /////////////////////////////////////////
////////////////////////////////////////////////////////////////////////////

void invia_misure_ASCII_usb(float * mis)
{
fprintf(usb,"%4.4f;%4.4f;%4.4f;%4.4f;%4.4f;%4.4f;%4.4f;%4.4f;%3.1f;%3.1f;%2.3f\r\n",
	mis[1],mis[2],mis[3],mis[4],mis[5],mis[6],mis[7],mis[8],mis[9],mis[10],mis[0]);
}


void invia_HEADER_USB()
{
disable_INTERRUPTS(INT_RDA);
fprintf(usb,"s1[v];s2[v];s3[v];s4[v];s5[v];s6[v];s7[v];s8[v];t[c];rh[%%];pwr[v]\r\n");
enable_INTERRUPTS(INT_RDA);
}

////////////////////////////////////////////////////////////////////////////
//////GESTIONE COMUNICAZIONI CON CPU////////////////////////////////////////
////////////////////////////////////////////////////////////////////////////
#int_rda
void rb0_isr()
{
disable_INTERRUPTS(INT_RDA);
usb_rx_buf[buffer_index]=fgetc(usb);
buffer_index++;
if(buffer_index==BUFFER_LENGHT) buffer_index = 0;
enable_INTERRUPTS(INT_RDA);
}


////////////////////////////////////////////////////////////////////////////
///////////////////////////MAIN///////////////////////////////////////////////
////////////////////////////////////////////////////////////////////////////
void main()
{
byte stepS5;
byte stepS6;
byte stepS7;
byte stepS8;
byte stepS1;
byte stepS3;
byte stepS4;
byte stepS2;
byte stepT;
byte stepRH;
byte stepPWR;
unsigned long sensCH0;
unsigned long sensCH1;
unsigned long sensCH2;
unsigned long sensS5;
unsigned long sensS6;
unsigned long sensS7;
unsigned long sensS8;
unsigned long sensS1;
unsigned long sensS3;
unsigned long sensS4;
unsigned long sensS2;
float tempBias;
float tempSens;
float RHBias;
float RHsens;
float V33;
float pwr33V;
port_b_pullups(true);
enable_INTERRUPTS(INT_RDA);
enable_interrupts(GLOBAL);

init:
buffer_index = 0;
buffer_counter = 0;
setup_adc_ports(ALL_ANALOG);
setup_adc(ADC_CLOCK_INTERNAL);

stepS5 = 0;
stepS6 = 0;
stepS7 = 0;
stepS8 = 0;
stepS1 = 0;
stepS3 = 0;
stepS4 = 0;
stepS2 = 0;
stepT = 0;
stepRH = 0;
stepPWR = 0;

tempBias=0.5;
tempSens=100;
RHBias=0.1515;
RHsens=157.23270440251572327044025157233;


ciclo:
if(buffer_index!=buffer_counter)
{
	if(buffer_index==0){usb_buffer_pointer = BUFFER_LENGHT-1;}
	else{usb_buffer_pointer = buffer_index-1;}
	switch ( usb_rx_buf[usb_buffer_pointer] ) {
	case 'i':
		disable_INTERRUPTS(INT_RDA);
		fprintf(usb,IDENTITY);
		enable_INTERRUPTS(INT_RDA);
		break;
	case 'h':
		disable_INTERRUPTS(INT_RDA);
		invia_HEADER_USB();
		enable_INTERRUPTS(INT_RDA);
		break;
	case 'g':
		disable_INTERRUPTS(INT_RDA);
		invia_misure_ASCII_usb(misure);
		enable_INTERRUPTS(INT_RDA);
		break;
	}
	buffer_counter = buffer_index;
}
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
